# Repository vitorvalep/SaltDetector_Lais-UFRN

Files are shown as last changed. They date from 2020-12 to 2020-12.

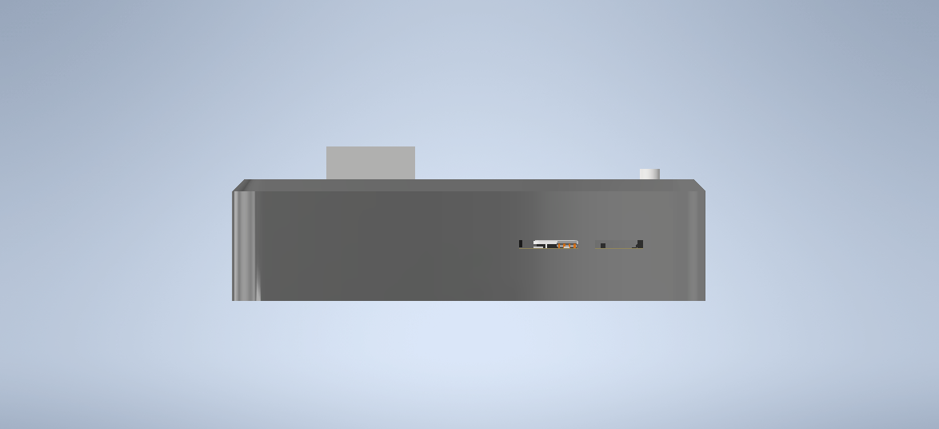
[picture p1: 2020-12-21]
3d_models/Montagem_case2.png

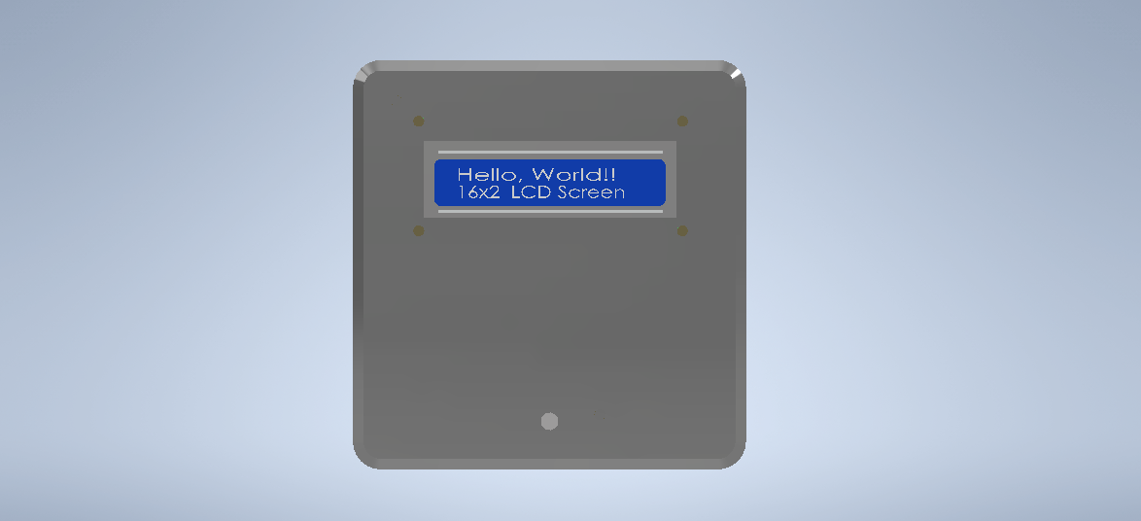
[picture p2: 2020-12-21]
3d_models/Montagem_case4.png

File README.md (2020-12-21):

# SaltDetector_Lais-UFRN

Projeto foi feito como parte da seleção para bolsista do Laboratório de Inovação Tecnológica em Saúde.
Este projeto consiste em um hardware capaz de identificar a presença de sal ou açúcar em água. Para isso o projeto foi dividido em 4 partes

1 - Simulação de parte do projeto utilizando a ferramenta tinkerCAD e plataforma arduino

2 - Codificação do firmware utilizando a plataforma Arduino

3 - Desenvolvimento do hardware utilizando a ferramenta da autodesk Eagle.

4 - Desenvolvimento de case de proteção do hardware

## O projeto da placa de circuito impresso contém:

1 - Microcontrolador atmega328p, sendo o cérebro do sistema.

2 - Amplificadores operacionais para amplificação do sinal medido pelos eletrodos. Estes circuitos devem ser alterados durante calibração e testes.

3 - Suporte para cartão SD para que os dados sejam salvos em csv para análises posteriores.

4 - RTC para manter o horário atualizado e fazer o controle dos arquivos salvos no SD card

5 - Sistema de carregamento e utilização de baterias do tipo Lithium ion.

6 - Sensor de corrente I²C para medição de corrente para medição de corrente nos eletrodos.

7 - Display LCD 16x2 para visualização de informações dos sensores.

O Hardware desenvolvido é capaz de medir a condutividade da água por meio de uma célula formada por 3 eletrodos. Para a medição da condutividade, utilizou-se amplificadores operacionais para amplificar o sinal medido pelos eletrodos. A informação de que existe sal ou açúcar na água se dá por meio de um lcd 16x2, que mostra a condutividade da água e se há sal ou açúcar no mesmo. O dispositivo funciona com bateria do tipo Lithium ion e pode ser recarregado por uma entrada micro USB.

O dispositivo também é capaz de realizar a voltametria cíclica, experimento que consiste em enviar uma onda triangular de tensão e observar os valores de tensão e corrente nos eletrodos da célula Por meio do sensor de corrente embutido no hardware pode-se medir a corrente que flui pelo eletrodo de trabalho e o conversor A/D do chip atmeg328p junto com os amplificadores operacionais obtém o valor da tensão sobre o eletrodo de referência e o eletrodo de trabalho. Após a varredura, duas informações são mostradas no LCD, que são os picos de corrente e tensão durante o experimento. Há um slot para cartão SD que guarda todos os valores em um arquivo csv, cujo nome é a data e horário da voltametria. Com esse arquivo pode-se exportar as informações e gerar gráficos para análises posteriores

## Melhorias para o projeto.

1 - Utilizar de um display TFT touch para plotar gráficos e mostrar mais informações sobre a voltametria cíclica, bem como melhorar a interação entre o operador e hardware

2 - Utilizar um chip de comunicação GSM para que os dados sejam enviados em tempo real para a nuvem e lá contenha todas as informações coletadas pelo operador, eliminando assim, o uso do cartão SD.

3 - Melhorias do case de proteção da placa

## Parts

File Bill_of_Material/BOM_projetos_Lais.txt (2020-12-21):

Partlist exported from C:/Users/Vitor/Documents/EAGLE/projects/Lais_sensor/esquematico.sch at 12/21/2020 12:58 PM

Part Value                         Device                        Package                       Description                                        CATEGORY  CREATED_BY    LABEL MANUFACTURER MPN      OPERATING_TEMP PACKAGE PART_STATUS POPULARITY PROD_ID   ROHS_COMPLIANT SERIES SPICEPREFIX SUB-CATEGORY THERMALLOSS TYPE VALUE           VOLTAGE_RATING
ACT  RED                           LEDCHIP-LED0805               CHIP-LED0805                  LED                                                                                                                                                                                                                                                          
BAT  CR1220                        CR1220THM                     CR1220-THM                    CR1216/CR1220/CR1225 12mm 3V lithium coin cell                                                                                                                                                                                                               
C1   22pF                          C_TANTALUM-2412(6032-METRIC)  CAPM6032X280                  Capacitor - Generic                                Capacitor                                                                                                                                                                                                 
C2   22pF                          C_TANTALUM-2412(6032-METRIC)  CAPM6032X280                  Capacitor - Generic                                Capacitor                                                                                                                                                                                                 
C3   0.1µF                         CAP_CERAMIC0805               0805                          Ceramic Capacitors                                                                                                                                                                                                                                           
C4   10uF                          10UF-1206-6.3V-20%            1206                          10.0µF ceramic capacitors                                                                                                                            CAP-10057                                                                 10uF                          
C5   1.0uF                         1.0UF-0603-16V-10%            0603                          1µF ceramic capacitors                                                                                                                               CAP-00868                                                                 1.0uF                         
C6   0.1uF                         0.1UF-0603-25V-5%             0603                          0.1µF ceramic capacitors                                                                                                                             CAP-08604                                                                 0.1uF                         
C7   10uF/10V                      CPOL-USA/3216-18R             A/3216-18R                    POLARIZED CAPACITOR, American symbol                                                                                                                                                                                                                         
C8   0.1uF                         C-USC0805K                    C0805K                        CAPACITOR, American symbol                                                                                                                                                                                                                                   
C9   0.1uF                         C-US025-025X050               C025-025X050                  CAPACITOR, American symbol                                                                                                                                                                                                                                   
CE                                 PINHD-1X1-BIGPOGO             1X1-BIGPOGO                   Pin header 1x1 for 0.1" spacing                                                                                                                                                                                                                              
IC1  UA741D                        UA741D                        SO08                          OP AMP                                                                                                                                    0                                                                                                                  
IC2  UA741D                        UA741D                        SO08                          OP AMP                                                                                                                                    0                                                                                                                  
IC3  4050D                         4050D                         SO16                          Hex non-inverting BUFFER                                                                                                                                                                                                                                     
IC4  LP298XS                       LP298XS                       SOT23-5L                                                                                                                                                                                                                                                                                   
IC5  DS1307                        DS1307                        DIL08                         DS1307                                                                                                                                                                                                                                                       
J2                                 I2C_STANDARD                  1X04                          SparkFun I2C Standard Pinout Header                                                                                                                                                                                                                          
JP1  JUMPER NO                     JUMPER-SMT_2_NO_NO-SILK       SMT-JUMPER_2_NO_NO-SILK       Normally open jumper                                                                                                                                                                                                                                         
JP3  BAT                           M01PTH                        1X01                          Header 1                                                                                                                                                                                                                                                     
JP4  JUMPER-SMT_2_NC_TRACE_NO-SILK JUMPER-SMT_2_NC_TRACE_NO-SILK SMT-JUMPER_2_NC_TRACE_NO-SILK Normally closed trace jumper                                                                                                                                                                                                                                 
JP10 GND-BAT                       M01PTH                        1X01                          Header 1                                                                                                                                                                                                                                                     
LED1 red                           LEDCHIP-LED0805               CHIP-LED0805                  LED                                                                                                                                                                                                                                                          
LED2 green                         LEDCHIP-LED0805               CHIP-LED0805                  LED                                                                                                                                                                                                                                                          
Q1   32.768                        CRYTALTC38H                   TC38H                         CRYSTAL                                                                                                                                                                                                                                                      
R1                                 R-US_R0805                    R0805                         RESISTOR, American symbol                                                                                                                                                            R                                                                       
R2   50                            R-US_R0805                    R0805                         RESISTOR, American symbol                                                                                                                                                            R                                                                       
R3   10k                           R-US_R0805                    R0805                         RESISTOR, American symbol                                                                                                                                                            R                                                                       
R4   10k                           R-US_R0805                    R0805                         RESISTOR, American symbol                                                                                                                                                            R                                                                       
R5   10K                           RESISTOR0805                  0805                          Resistors                                                                                                                                                                                                                                                    
R6   10K                           RESISTOR0805                  0805                          Resistors                                                                                                                                                                                                                                                    
R7   10K                           RESISTOR0805                  0805                          Resistors                                                                                                                                                                                                                                                    
R8   10K                           RESISTOR0805                  0805                          Resistors                                                                                                                                                                                                                                                    
R9   0.1/1% (PT2512FK-070R1L)      RESISTOR2512                  2512                          Resistors                                                                                                                                                                                                                                                    
R10  100k                          R-US_R0805                    R0805                         RESISTOR, American symbol                                                                                                                                                            R                                                                       
R11  100k                          R-US_R0805                    R0805                         RESISTOR, American symbol                                                                                                                                                            R                                                                       
R12  100k                          R-US_R0805                    R0805                         RESISTOR, American symbol                                                                                                                                                            R                                                                       
R13  100k                          R-US_R0805                    R0805                         RESISTOR, American symbol                                                                                                                                                            R                                                                       
R14  2.4k                          2.49KOHM-0603-1/10W-1%        0603                          2.49kΩ resistor                                                                                                                                      RES-09568                                                                 2.49k                         
R15  4.7k                          4.7KOHM-0603-1/10W-1%         0603                          4.7kΩ resistor                                                                                                                                       RES-07857                                                                 4.7k                          
R16  100                           RESISTOR0603-RES              0603-RES                      Resistor                                                                                                                                                                                                                                                     
R17  1k                            1KOHM-0603-1/10W-1%           0603                          1kΩ resistor                                                                                                                                         RES-07856                                                                 1k                            
R18  330                           330OHM-0603-1/10W-1%          0603                          330Ω resistor                                                                                                                                        RES-00818                                                                 330                           
R19  330                           330OHM-0603-1/10W-1%          0603                          330Ω resistor                                                                                                                                        RES-00818                                                                 330                           
R20  1K                            R-US_R0805                    R0805                         RESISTOR, American symbol                                                                                                                                                                                                                                    
R21  100k                          R-US_R0805                    R0805                         RESISTOR, American symbol                                                                                                                                                            R                                                                       
R22  2.2K                          R-US_0207/10                  0207/10                       RESISTOR, American symbol                                                                                                                                                                                                                                    
R23  2.2k                          R-US_0207/10                  0207/10                       RESISTOR, American symbol                                                                                                                                                                                                                                    
RE                                 PINHD-1X1-BIGPOGO             1X1-BIGPOGO                   Pin header 1x1 for 0.1" spacing                                                                                                                                                                                                                              
S1   SWITCH-OMRON_B3U-1000P        SWITCH-OMRON_B3U-1000P        SWITCH-OMRON_B3U-1000P        SMD Tactile Switch - Ultra Small                                                                                                                                                                                                                             
SJ1                                SOLDERJUMPERREFLOW_NOPASTE    SOLDERJUMPER_REFLOW_NOPASTE   SMD Solder JUMPER                                                                                                                                                                                                                                            
SJ2                                SOLDERJUMPERREFLOW_NOPASTE    SOLDERJUMPER_REFLOW_NOPASTE   SMD Solder JUMPER                                                                                                                                                                                                                                            
SW1  PTS645SM43SMTR92LFS           PTS645SM43SMTR92LFS           PTS645-SMT-6MM                SWITCH TACTILE SPST-NO 0.05A 12V                                                                                                                                                                                                                             
U$1  DIO5158                       DIO5158                       SOIC-8                                                                                                                                                                                                                                                                                     
U$7  DW01-P                        DW01-P                        SOT23-6L                      One Cell Lithium-ion/Polymer Battery Protection IC                                                                                                                                                                                                           
U$8  FS8205A                       FS8205A                       TSSOP8                                                                                                                                                                                                                                                                                     
U$9  USB-MICROB-POWERONLY          USB-MICROB-POWERONLY          USB-MICROB-POWERONLY                                                                                                                                                                                                                                                                       
U1   ATMEGA328P_TQFP               ATMEGA328P_TQFP               TQFP32-08                     Popular 328P in QFP                                                                                                                                  IC-09069                                                                  ATMEGA328P_TQFP               
U2   INA219BIDCNT                  INA219                        SOT23-8                       INA219 - I2C Current/Power Monitor                                                                                                                                                                                                                           
WE                                 PINHD-1X1-BIGPOGO             1X1-BIGPOGO                   Pin header 1x1 for 0.1" spacing                                                                                                                                                                                                                              
X1   16MHz                         49S/18PF                      XTAL_HC49                     Crystal                                                      PCBLayout.com       Xinhunjing   49S/18PF                SMD                                                                                                                                    
X2   MICROSD                       MICROSD                       MICROSD                       Micro-SD / Transflash card holder with SPI pinout                                                                                                                                                                                                            
LCD1 LCD-16X2SILK      LCD-16X2SILK      LCD-16X2          Standard text-only 16x2 parallel input LCD                        LCD-00255
U$1  LCD-I2C-CONVERTER LCD-I2C-CONVERTER LCD-I2C-CONVERTER I2C Bus to 4-Bit Parallel LCD Interface with LED backlight driver

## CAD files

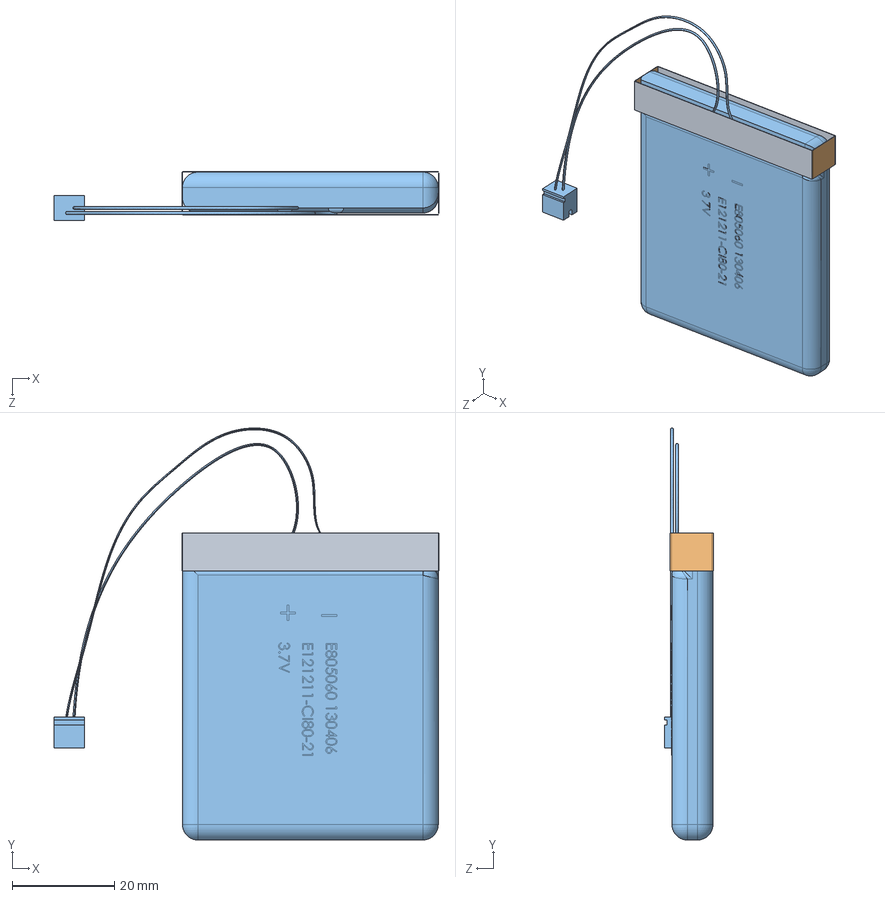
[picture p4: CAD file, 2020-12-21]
3d_models/Case/Battery 2500mAh.STEP
75.2 x 80.5 x 9.55 mm

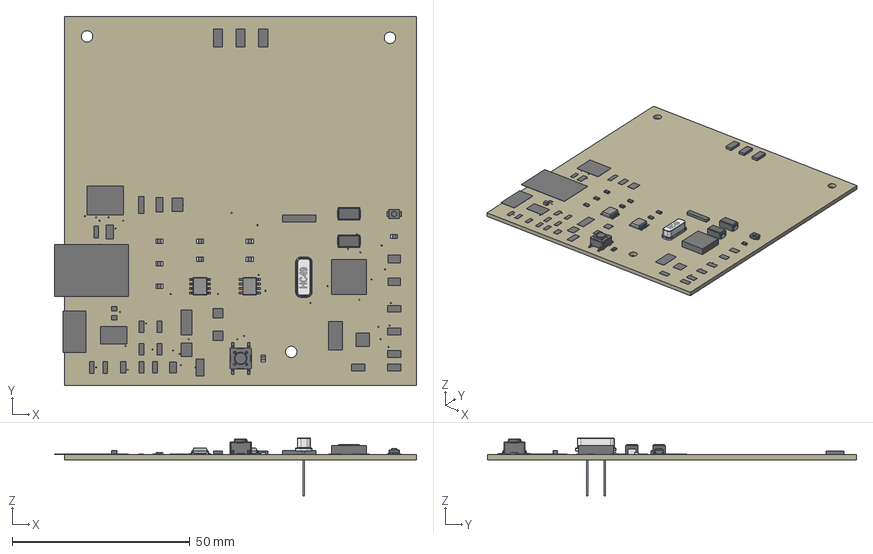
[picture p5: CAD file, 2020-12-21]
3d_models/PCB/esquematico v3.step
101.9 x 103.8 x 16.3 mm
Board
SO16
SWITCH-OMRON_B3U-1000P
CAPM6032X280 x 2
XTAL_HC49
SOIC-8
USB-MICROB-POWERONLY
PTS645-SMT-6MM
Ferrite x 9
Contact x 18
1X04
TQFP32-08
SMT-JUMPER_2_NC_TRACE_NO-SILK
SMT-JUMPER_2_NO_NO-SILK
0603-RES
1X01 x 2
TSSOP8
1X1-BIGPOGO x 3
A/3216-18R
C0805K
CHIP-LED0805 x 3
MICROSD
R0805 (1)
SOT23-5L
SO08 x 2
SOT23-6L
SOLDERJUMPER_REFLOW_NOPASTE x 2
SOT23-8

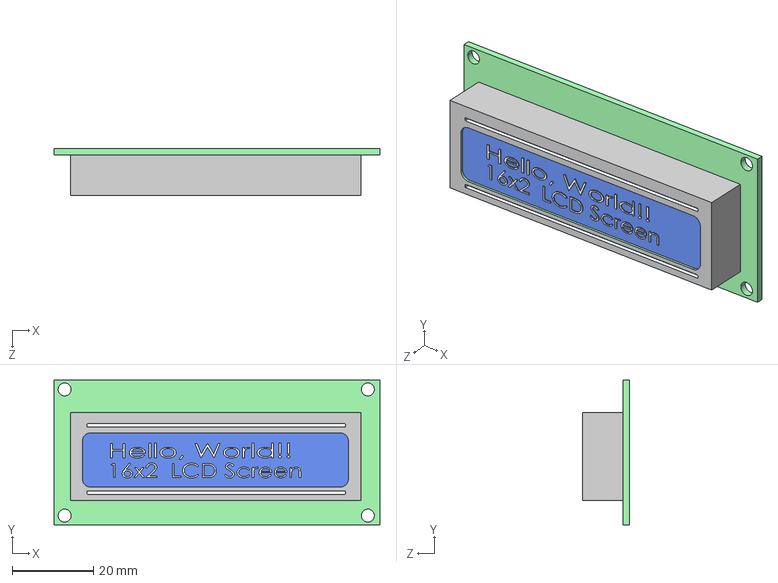
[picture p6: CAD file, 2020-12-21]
3d_models/Case/LCD Screen.STEP
80.1 x 35.5 x 11.5 mm

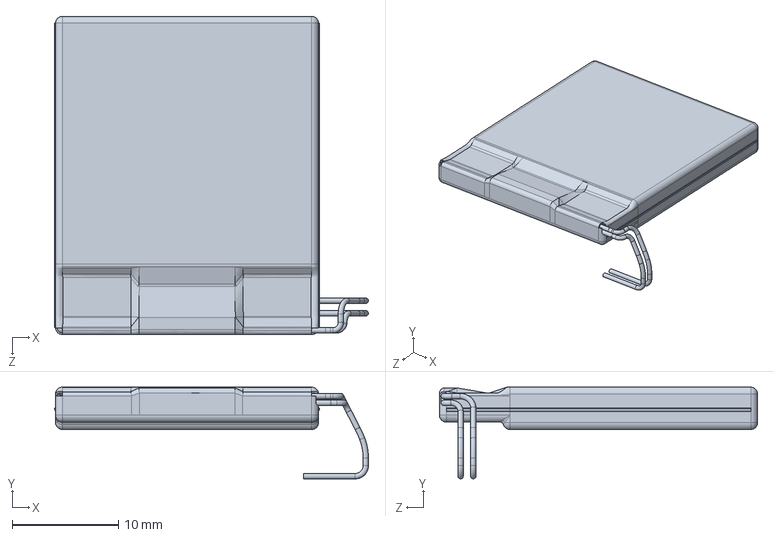
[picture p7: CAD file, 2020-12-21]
3d_models/Case/402530, LiPo battery 300 mAh.SLDPRT
29.6 x 8.66 x 30.0 mm

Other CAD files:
3d_models/Case/Base.ipt
3d_models/Case/Montagem_case.iam
3d_models/Case/OldVersions/Base.0001.ipt
3d_models/Case/OldVersions/Tampa.0001.ipt
3d_models/Case/Tampa.ipt
3d_models/PCB/Inventor_files/0603 (1).ipt
3d_models/PCB/Inventor_files/0603-RES.ipt
3d_models/PCB/Inventor_files/0603.ipt
3d_models/PCB/Inventor_files/0805.ipt
3d_models/PCB/Inventor_files/1206.ipt
3d_models/PCB/Inventor_files/1X01.ipt
3d_models/PCB/Inventor_files/1X04.ipt
3d_models/PCB/Inventor_files/1X1-BIGPOGO.ipt
3d_models/PCB/Inventor_files/2512.ipt
3d_models/PCB/Inventor_files/A_3216-18R.ipt
3d_models/PCB/Inventor_files/Board.ipt
3d_models/PCB/Inventor_files/C0805K.ipt
3d_models/PCB/Inventor_files/CAPM6032X280.ipt
3d_models/PCB/Inventor_files/CHIP-LED0805.ipt
3d_models/PCB/Inventor_files/Contact.ipt
3d_models/PCB/Inventor_files/Ferrite.ipt
3d_models/PCB/Inventor_files/MICROSD.ipt
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

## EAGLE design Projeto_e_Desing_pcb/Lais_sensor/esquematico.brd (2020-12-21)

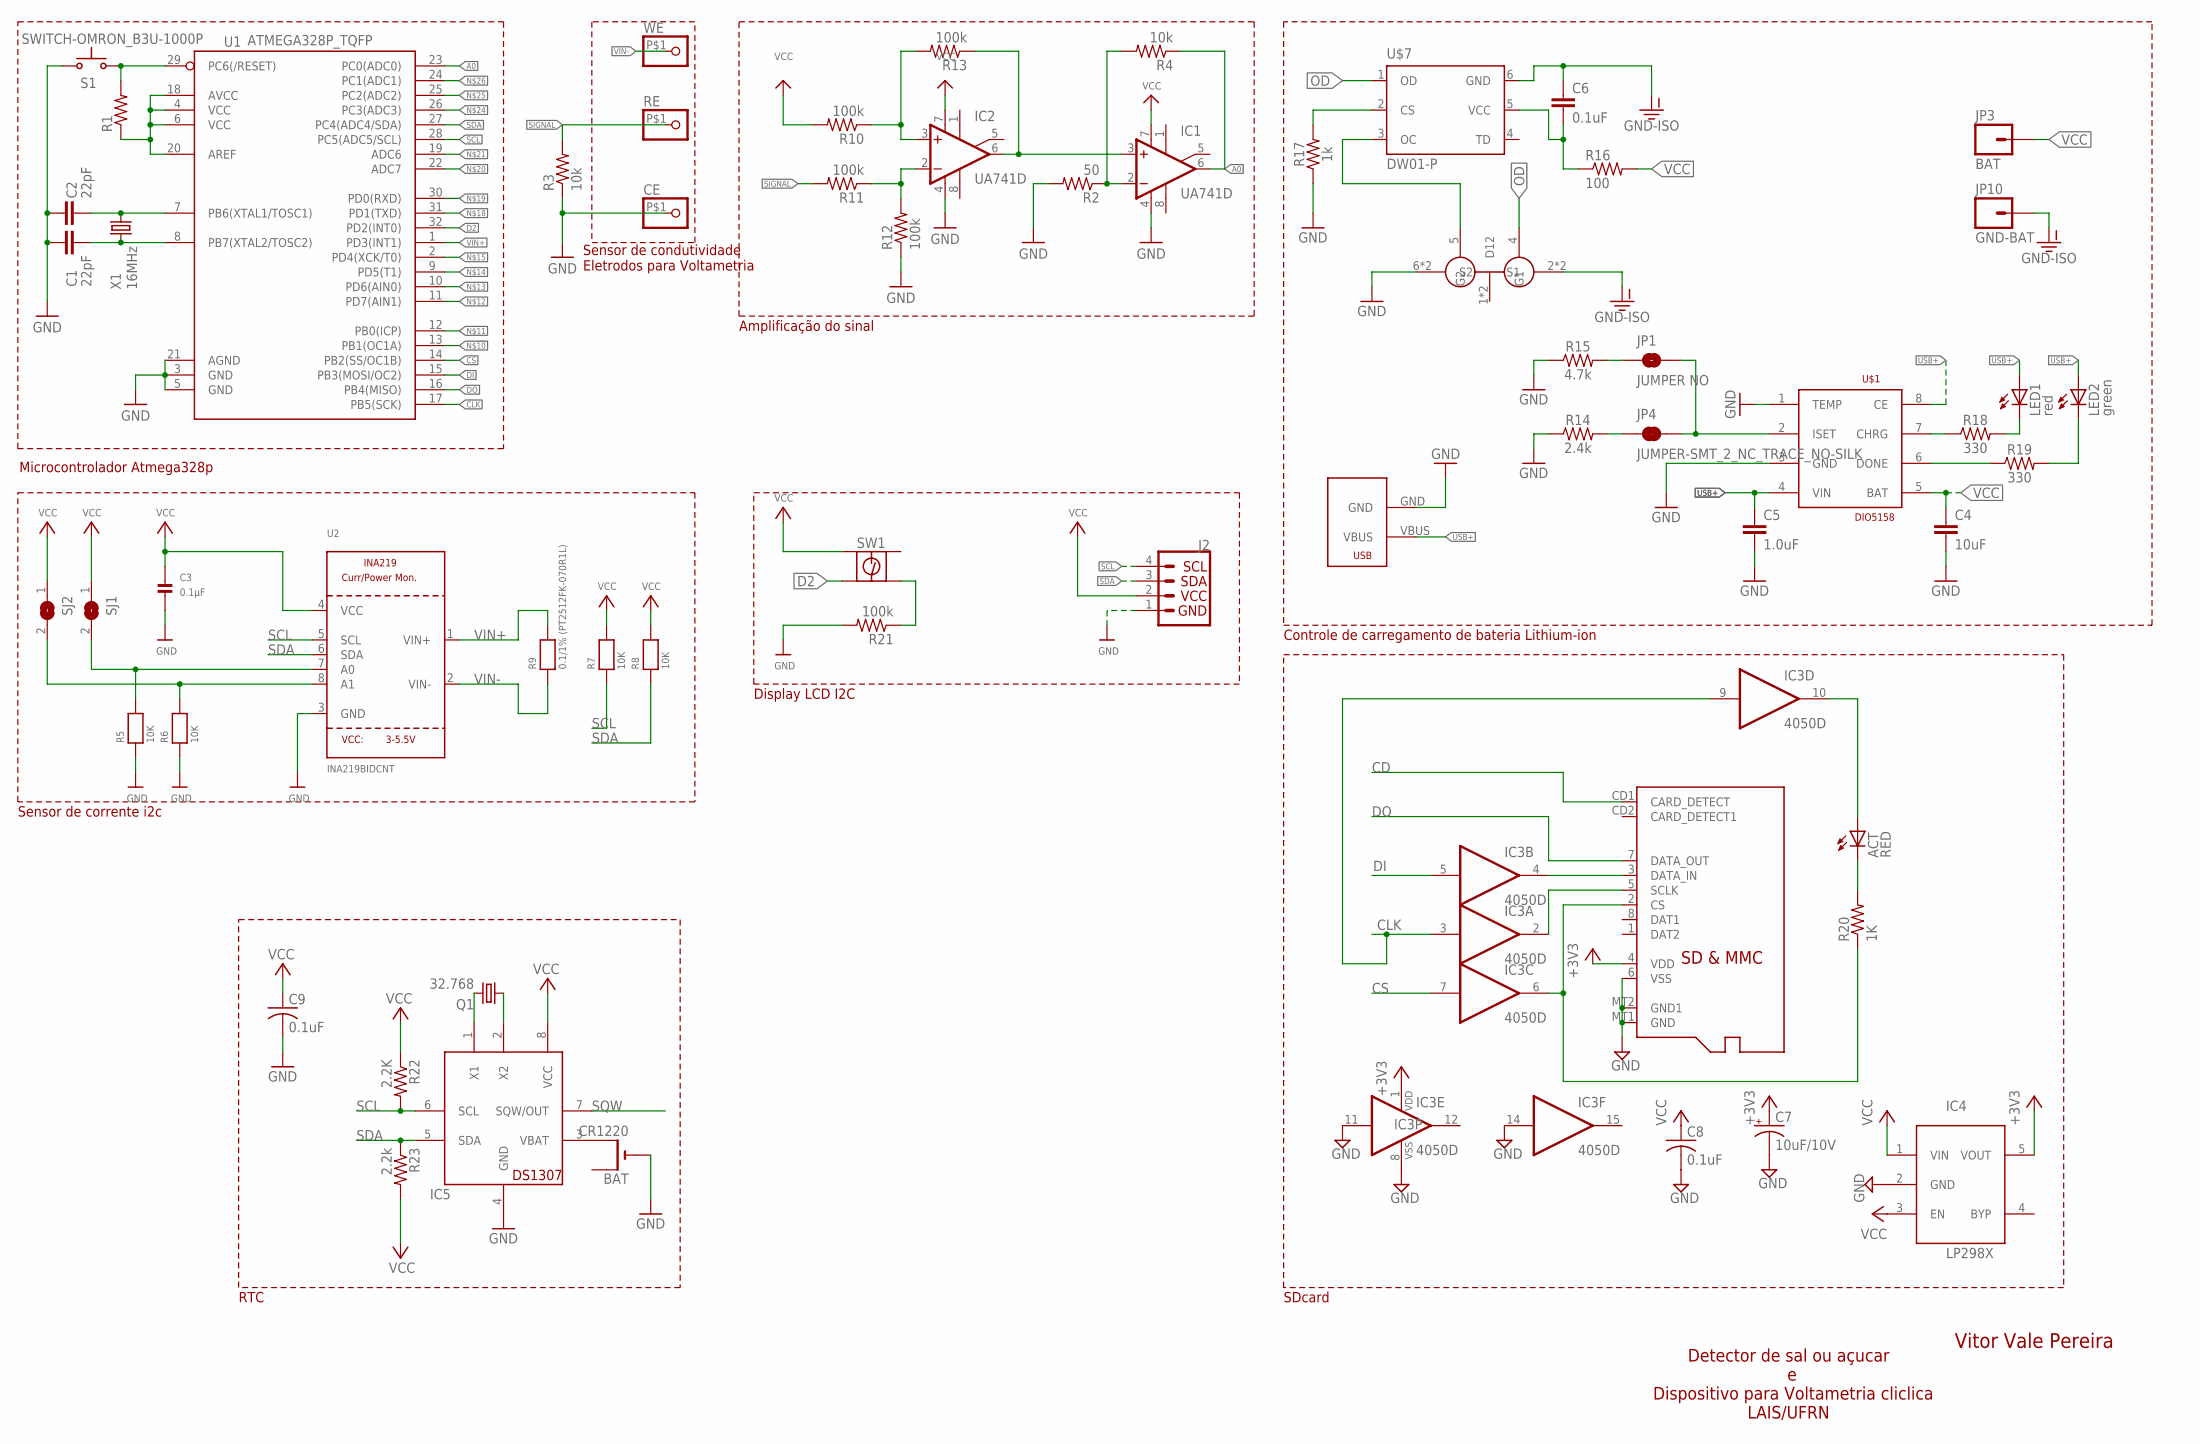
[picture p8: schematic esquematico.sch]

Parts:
ACT: RED; CHIP-LED0805
BAT: CR1220; CR1220-THM
C1, C2: 22pF; CAPM6032X280
C3: 0.1µF; 0805
C4: 10uF; 1206
C5: 1.0uF; 0603
C6: 0.1uF; 0603
C7: 10uF/10V; A/3216-18R
C8: 0.1uF; C0805K
C9: 0.1uF; C025-025X050
CE: PINHD-1X1-BIGPOGO; 1X1-BIGPOGO
IC1, IC2: UA741D; SO08
IC3: 4050D; SO16
IC4: LP298XS; SOT23-5L
IC5: DS1307; DIL08
J2: I2C_STANDARD; 1X04
JP1: JUMPER NO; SMT-JUMPER_2_NO_NO-SILK
JP3: BAT; 1X01
JP4: JUMPER-SMT_2_NC_TRACE_NO-SILK; SMT-JUMPER_2_NC_TRACE_NO-SILK
JP10: GND-BAT; 1X01
LED1: red; CHIP-LED0805
LED2: green; CHIP-LED0805
Q1: 32.768; TC38H
R1: R-US_R0805; R0805
R2: 50; R0805
R3, R4: 10k; R0805
R5, R6, R7, R8: 10K; 0805
R9: 0.1/1% (PT2512FK-070R1L); 2512
R10, R11, R12, R13, R21: 100k; R0805
R14: 2.4k; 0603
R15: 4.7k; 0603
R16: 100; 0603-RES
R17: 1k; 0603
R18, R19: 330; 0603
R20: 1K; R0805
R22: 2.2K; 0207/10
R23: 2.2k; 0207/10
RE: PINHD-1X1-BIGPOGO; 1X1-BIGPOGO
S1: SWITCH-OMRON_B3U-1000P
SJ1, SJ2: SOLDERJUMPERREFLOW_NOPASTE; SOLDERJUMPER_REFLOW_NOPASTE
SW1: PTS645SM43SMTR92LFS; PTS645-SMT-6MM
U1: ATMEGA328P_TQFP; TQFP32-08
U2: INA219BIDCNT; SOT23-8
U$1: DIO5158; SOIC-8
U$7: DW01-P; SOT23-6L
U$8: FS8205A; TSSOP8
U$9: USB-MICROB-POWERONLY
WE: PINHD-1X1-BIGPOGO; 1X1-BIGPOGO
X1: 16MHz; XTAL_HC49
X2: MICROSD

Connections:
+3V3: C7.+, IC3.1 (VDD), IC4.5 (VOUT), X2.4 (VDD)
A0: IC1.6 (OUT), R4.1, U1.23 (PC0(ADC0))
CD: X2.CD1 (CARD_DETECT)
CHRG: R18.1, U$1.7 (CHRG)
CLK: IC3.3 (I), IC3.9 (I), U1.17 (PB5(SCK))
CS: IC3.7 (I), U1.14 (PB2(SS/OC1B))
D2: SW1.P$3 (3), U1.32 (PD2(INT0))
DI: IC3.5 (I), U1.15 (PB3(MOSI/OC2))
DO: U1.16 (PB4(MISO)), X2.7 (DATA_OUT)
DONE: R19.1, U$1.6 (DONE)
GND: BAT.-, C1.1, C2.1, C3.2, C4.2, C5.2, C7.-, C8.2, C9.2, CE.P$1, IC1.4 (V-), IC2.4 (V-), IC3.8 (VSS), IC3.11 (I), IC3.14 (I), IC4.2 (GND), IC5.4 (GND), J2.1, R2.2, R3.1, R5.1, R6.1, R12.1, R14.1, R15.1, R17.1, R21.2, S1.1, U1.3 (GND), U1.5 (GND), U1.21 (AGND), U2.3 (GND), U$1.1 (TEMP), U$1.3 (GND), U$8.6 (S2), U$8.7 (S2), U$9.GND, X2.6 (VSS), X2.MT1 (GND), X2.MT2 (GND1)
GND-ISO: C6.1, JP10.1, U$7.6 (GND), U$8.2 (S1), U$8.3 (S1)
ISET: JP1.2, JP4.2, U$1.2 (ISET)
LED1: LED1.C, R18.2
LED2: LED2.C, R19.2
unnamed: C2.2, U1.7 (PB6(XTAL1/TOSC1)), X1.2
unnamed: C1.2, U1.8 (PB7(XTAL2/TOSC2)), X1.1
unnamed: R1.2, S1.2 (S), U1.29 (PC6(/RESET))
unnamed: IC1.2 (-IN), R2.1, R4.2
unnamed: R21.1, SW1.P$4 (4)
unnamed: R6.2, SJ2.2, U2.8 (A1)
unnamed: IC5.1 (X1), Q1.2
unnamed: IC2.3 (+IN), R10.1, R13.2
unnamed: IC5.2 (X2), Q1.1
unnamed: IC2.2 (-IN), R11.1, R12.2
unnamed: IC1.3 (+IN), IC2.6 (OUT), R13.1
unnamed: R5.2, SJ1.2, U2.7 (A0)
unnamed: JP4.1, R14.2
unnamed: JP1.1, R15.2
unnamed: R17.2, U$7.2 (CS)
unnamed: U$7.3 (OC), U$8.5 (G2)
unnamed: ACT.A, IC3.10 (O)
unnamed: IC3.2 (O), X2.5 (SCLK)
unnamed: IC3.6 (O), R20.1, X2.2 (CS)
unnamed: ACT.C, R20.2
unnamed: IC3.4 (O), X2.3 (DATA_IN)
unnamed: BAT.+2 (+1), IC5.3 (VBAT)
OD: U$7.1 (OD), U$8.4 (G1)
SCL: IC5.6 (SCL), J2.4, R7.1, R22.2, U1.28 (PC5(ADC5/SCL)), U2.5 (SCL)
SDA: IC5.5 (SDA), J2.3, R8.1, R23.1, U1.27 (PC4(ADC4/SDA)), U2.6 (SDA)
SIGNAL: R3.2, R11.2, RE.P$1
SQW: IC5.7 (SQW/OUT)
USB+: C5.1, LED1.A, LED2.A, U$1.4 (VIN), U$1.8 (CE), U$9.VBUS
VCC: C3.1, C4.1, C8.1, C9.1, IC1.7 (V+), IC2.7 (V+), IC4.1 (VIN), IC4.3 (EN), IC5.8 (VCC), J2.2, JP3.1, R1.1, R7.2, R8.2, R10.2, R16.2, R22.1, R23.2, SJ1.1, SJ2.1, SW1.P$1 (1), U1.4 (VCC), U1.6 (VCC), U1.18 (AVCC), U1.20 (AREF), U2.4 (VCC), U$1.5 (BAT)
VCC-DW: C6.2, R16.1, U$7.5 (VCC)
VIN+: R9.2, U1.1 (PD3(INT1)), U2.1 (VIN+)
VIN-: R9.1, U2.2 (VIN-), WE.P$1

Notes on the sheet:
Sensor de condutividade Eletrodos para Voltametria
Sensor de corrente i2c
Amplificação do sinal
Microcontrolador Atmega328p
Controle de carregamento de bateria Lithium-ion
SDcard
Display LCD I2C
RTC
Vitor Vale Pereira
Detector de sal ou açucar e Dispositivo para Voltametria cliclica LAIS/UFRN

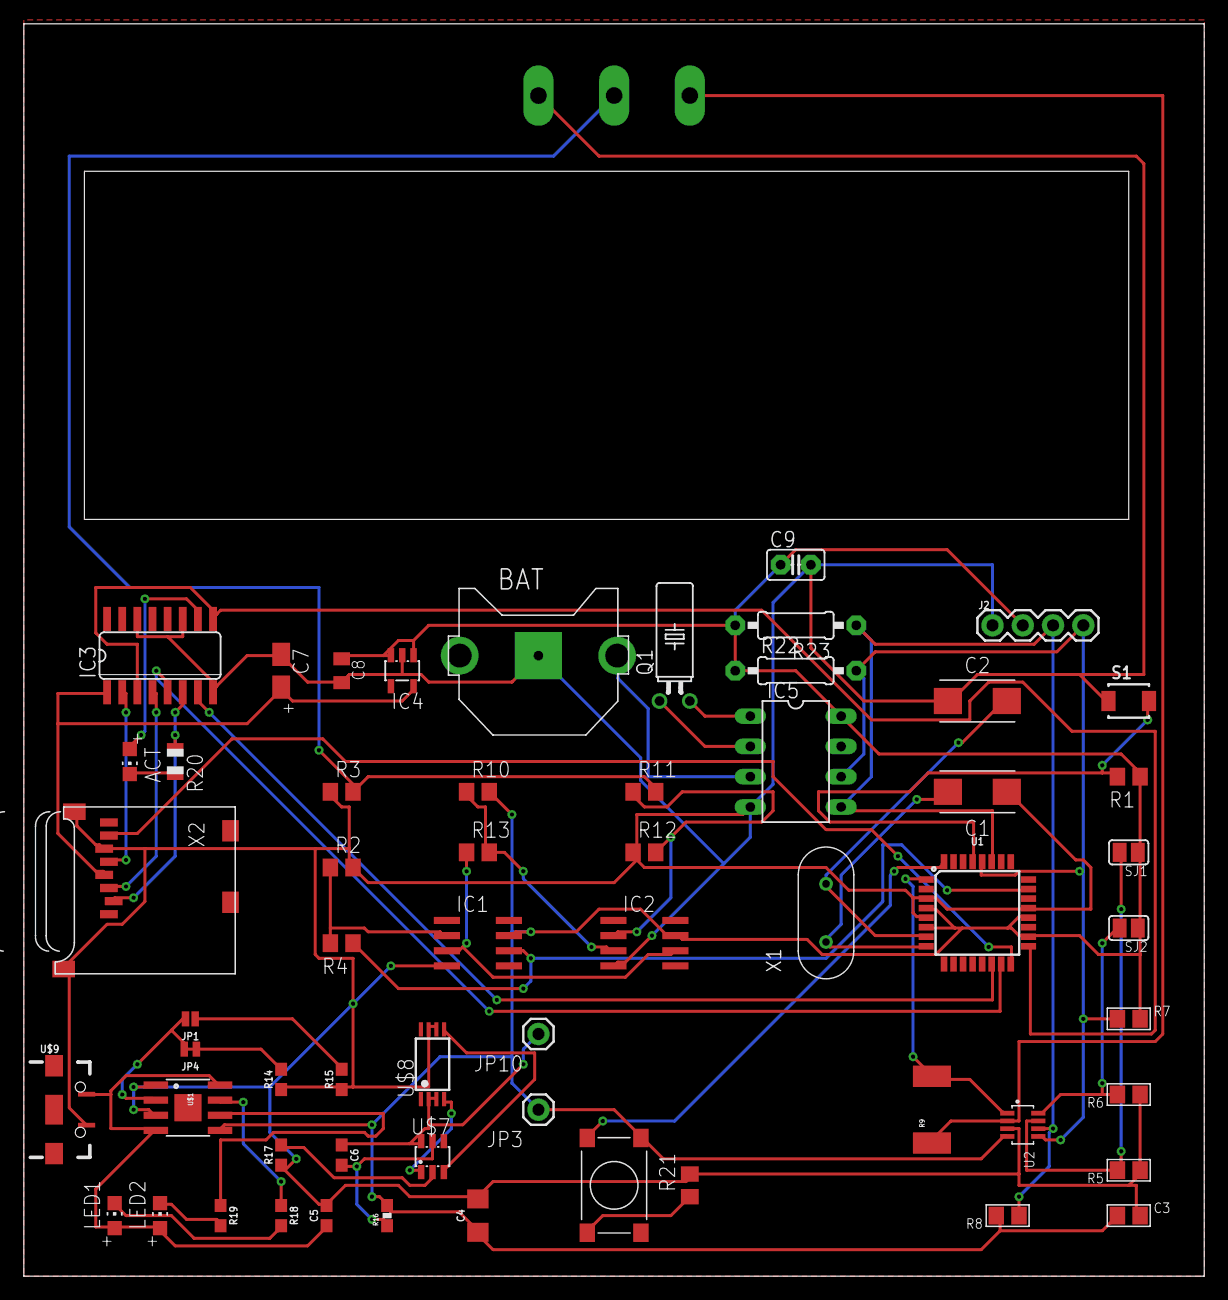
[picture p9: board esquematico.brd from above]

Board: 2 copper layers, 99.0 x 105.1 mm, 62 parts (0 on the bottom side), 45 nets.

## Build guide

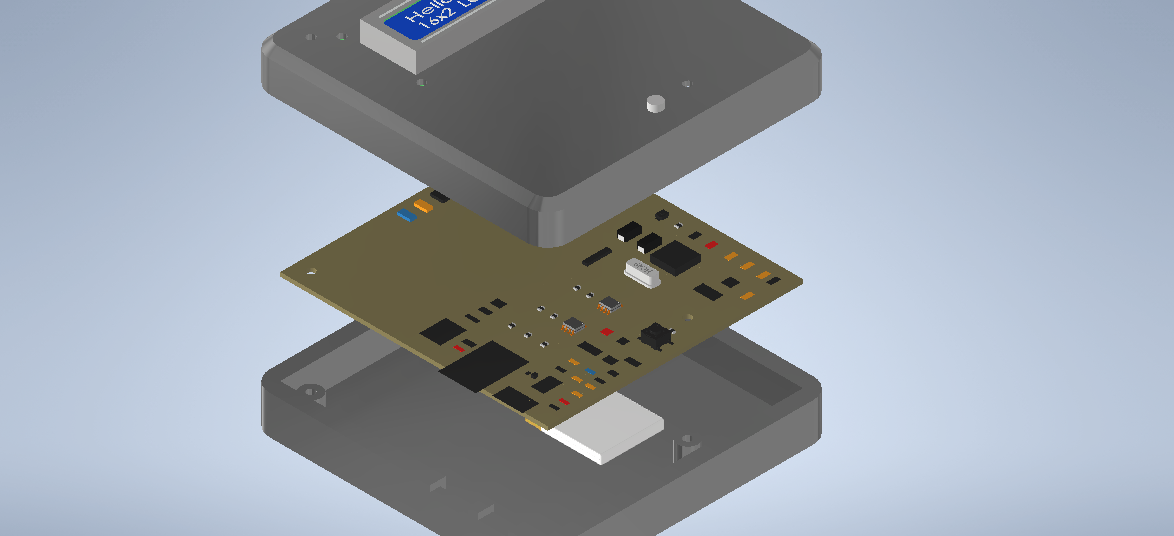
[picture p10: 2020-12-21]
3d_models/Montagem_case5.png

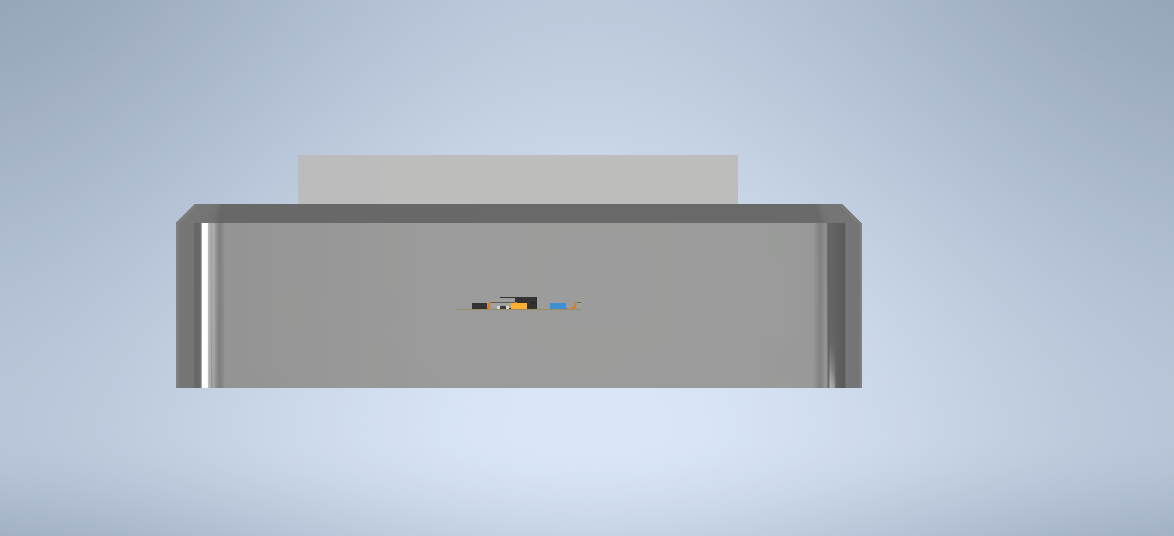
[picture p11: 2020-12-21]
3d_models/Montagem_case3.png

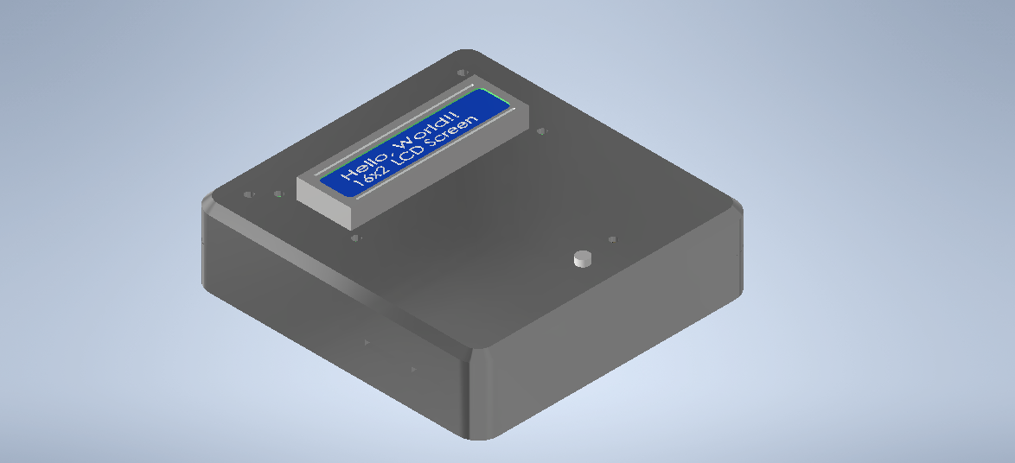
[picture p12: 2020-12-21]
3d_models/Montagem_case1.png

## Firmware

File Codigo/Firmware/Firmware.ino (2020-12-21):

/*
   Firmware para o hardware de leitura da condutividade da água
   permitindo a identificação de sal ou açucar no mesmo.

   Projeto realizado para seleção de bolsistas para o projeto
   sífilis não do Lais/UFRN para a área de sistemas embarcados
   e biosensores.

   Primeira versão do firmware(prototipo)
*/
//Bibliotecas
#include <Wire.h>
#include <Adafruit_INA219.h>  //biblioteca do sensor de corrente
#include <LiquidCrystal_I2C.h>  //biblioteca lcd i2c
#include <SPI.h>
#include <SD.h> //biblioteca SD card
#include <DS1307.h> //bilbioteca RTC

//funções
float max_value(float m, float n);
void media(float v, float i);

//Init RTC
// Init the DS1307
DS1307 rtc(4, 5);

//instancia do SDcard
File file;
byte chip_select = 10;


const int LCD_addr = 0x3F;
const int LCD_chars = 16;
const int LCD_lines = 2;
LiquidCrystal_I2C lcd(LCD_addr, LCD_chars, LCD_lines); //Indica o endereço do LCD  - 0x3F, com 16 caracteres e 2 linhas


//sensor de corrente
const int INA_addr = 0x40;  //endereço  INA219
Adafruit_INA219 ina219(INA_addr); // indica o endereço do INA219 - 0x40
float corrente_mA = 0;
float voltage = 0;


//váriaveis condutividade da agua
float condut_agua = 0;
float A_eletrodo = 0.001; //valor arbitrario
float L_eletrodo = 0.01; //valor arbitrario
float limite_condut = 500;

//Variáveis utilizadas na voltametria ciclica
byte ciclos = 5;
int tempo_degrau = 50;
float velocidade_varredura = (5 / 256) / tempo_degrau;
float I_max = 0;
float V_max = 0;
float I_med = 0;
float V_med = 0;


//Variavel de tela
boolean tela = 0;

void setup() {
  //Inicialização RTC
  rtc.halt(false);
  //Depois de configurado, pode ser comentado
  //rtc.setDOW(SUNDAY);        // dia da semana
  //rtc.setTime(12, 0, 0);     // hora (24hr formato)
  //rtc.setDate(3, 10, 2010);   // data


  //Inicialização do INA219
  ina219.begin();

  //incialização do LCD
  lcd.init();
  lcd.clear();
  lcd.backlight();

  //Tela de inicialização
  lcd.setCursor(0, 0);
  lcd.print("Leitura da");
  lcd.setCursor(0, 1);
  lcd.print("condutividade");
  delay(2000);

  //configura pino 3 como saída, esse pino vai servir como
  //fonte de tensão para o divisor de tensão e para leitura
  //dos valores de condutividade
  pinMode(3, 1);

  //SD card init
  if (!SD.begin(chip_select)) {
    lcd.print("Falha no SD");
    lcd.print("Verifique cartao");
    while (1);
  }

}

void loop() {
  if (digitalRead(2)) {
    tela = !tela;
  }
  if (!tela) {
    //Leitura da condutividade da agua
    digitalWrite(3, 1);
    voltage = analogRead(A0) * (5 / 1023);
    corrente_mA = ina219.getCurrent_mA();
    condut_agua = ((corrente_mA * L_eletrodo) / (voltage * A_eletrodo)) / 201.0; //201 é o valor do ganho do aplificador operacional
    //que faz a amplificação do sinal vindo do eletrodo

    lcd.setCursor(0, 0);
    lcd.print("con: "); lcd.print(condut_agua); lcd.print("S/cm");
    lcd.setCursor(0, 1);
    if (condut_agua > limite_condut) {
      lcd.print("agua com sal");
    } else {
      lcd.print("agua sem sal");
    }

  }

  if (tela) {
    //voltametria ciclica
    lcd.clear();
    lcd.setCursor(0, 0);
    lcd.print("Voltametria");
    lcd.setCursor(0, 1);
    lcd.print("Aguarde");
    //Criando arquivo com nome da data e hora da voltametria
    String file_name = rtc.getDateStr();
    file_name = file_name + "_" + rtc.getTimeStr() + ".csv";
    file = SD.open(file_name, FILE_WRITE);
    //titulos das colunas do arquivo
    file.print("Tensão Corrente");

    for (int j = 0; j < ciclos; j++) {
      //Formação da onda triangular para a voltametria ciclica
      for (int i = 0; i < 256; i++) {
        analogWrite(3, i);

        //Leitura da tensão entre o eletrodo de trabalho e de referencia
        voltage = analogRead(A0) * (5 / 1023);

        //corrente passando pelo eletrodo de trabalho
        corrente_mA = ina219.getCurrent_mA();

        //Valor Maximo
        I_max = max_value(I_max, corrente_mA);
        V_max = max_value(V_max, voltage);

        //salvando dados no formato CSV para analises posteriores
        file.print(voltage);
        file.print(" ");
        file.println(corrente_mA);

        delay(tempo_degrau);
      }

      for (int i = 255; i > 0; i--) {
        analogWrite(3, i);

        //Leitura da tensão entre o eletrodo de trabalho e de referencia
        voltage = analogRead(A0) * (5 / 1023);

        //corrente passando pelo eletrodo de trabalho
        corrente_mA = ina219.getCurrent_mA();

        //Valor Maximo
        I_max = max_value(I_max, corrente_mA);
        V_max = max_value(V_max, voltage);

        //salvando dados no formato CSV para analises posteriores
        file.print(voltage);
        file.print(" ");
        file.println(corrente_mA);

        delay(tempo_degrau);
      }

    }
    file.close();
    lcd.clear();
    lcd.setCursor(0, 0);
    lcd.print("I_max: "); lcd.print(I_max);
    lcd.setCursor(0, 1);
    lcd.print("V_max: "); lcd.print(V_max);
    
    while (tela) {
      if (digitalRead(2)) {
        tela = !tela;
        delay(300);
      }
    }
  }
}


float max_value(float m, float n) {
  if (m > n) {
    return m;
  } else {
    return n;
  }
}

void media(float v, float i) {
  V_med = (V_med + v) / 2;
  I_med = (I_med + i) / 2;
}

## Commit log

2020-12-21 primeiro commit
    [BOM_projetos_Lais.csv, BOM_projetos_Lais.xlsx, copper_bottom.gbr, copper_top.gbr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]
2020-12-21 add case
    [0603 (1).ipt, 0603-RES.ipt, 0603.ipt, 0805.ipt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]

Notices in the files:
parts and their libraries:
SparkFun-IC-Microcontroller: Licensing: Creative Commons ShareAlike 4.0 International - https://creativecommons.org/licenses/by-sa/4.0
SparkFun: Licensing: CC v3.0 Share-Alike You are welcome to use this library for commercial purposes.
